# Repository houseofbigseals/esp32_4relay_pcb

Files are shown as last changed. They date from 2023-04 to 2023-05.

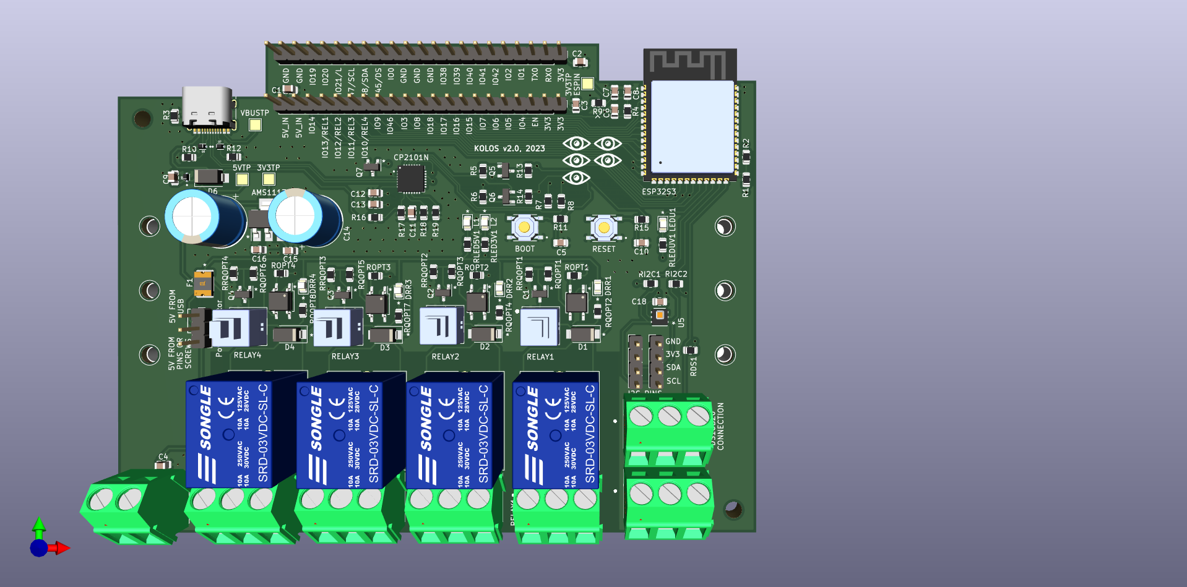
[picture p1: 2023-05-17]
esp32_4_relay3.png

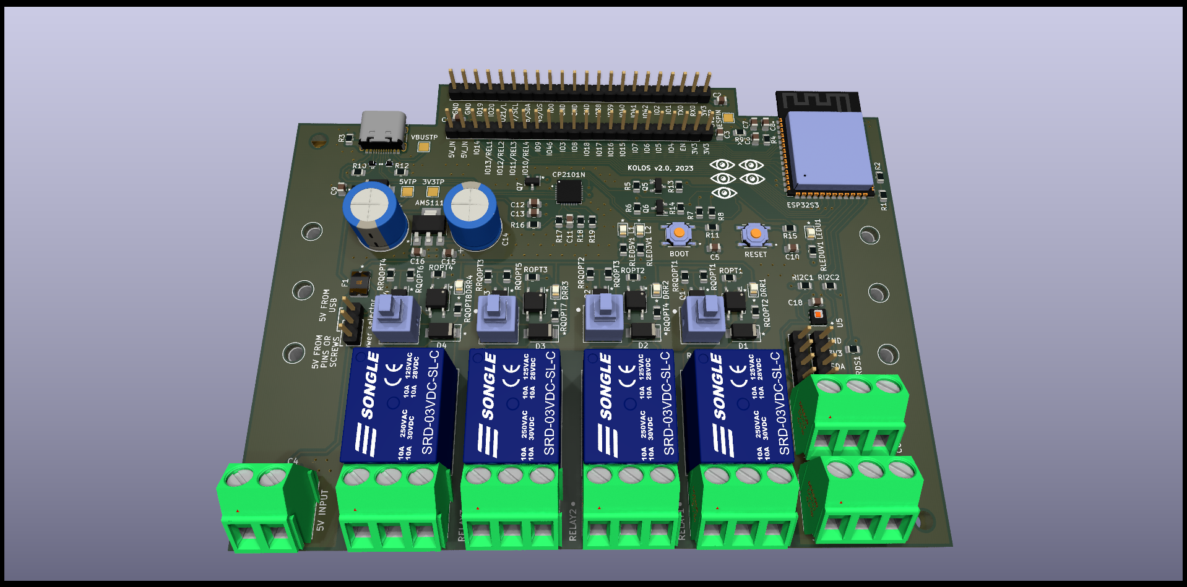
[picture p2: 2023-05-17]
esp32_4_relay.png

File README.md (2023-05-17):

KOLOS is an automation module based on ESP32-S3, designed for remote control of laboratory equipment - AC devices, sensors, indicators. Designed to manage environmental control systems for laboratory greenhouses with higher plants.  

Designed on a 4-layer printed circuit board, has dimensions of 124x95 mm.  
Powered by 5V via USB-C or screw connector, it has built-in surge protection with a self-resetting fuse. ESP32 is powered by a built-in AMS-1117-3.3 stabilizer.  
The board has expansion pins for connecting additional equipment to the controller, as well as screw connectors for connecting sensors using the 1-Wire protocol. The firmware of the controller and communication with the PC is done through the built-in USB-UART converter CP2102N. The board contains four relay channels controlled via an optocoupler and an HDC1080 temperature-humidity sensor.  
Mounting can be done in the housing with M3 screws or on a DIN rail, for which fasteners are provided.  
The firmware is implemented on the basis of the ESP-HOME framework for integrating the product into the Home Assistant environment. The system is configured so that the user can securely access the board remotely, via a Wireguard network, or locally.  

The pcb contains:  
- 4 5v relay module
- buttons for manual switching of the relay state in an emergency situation  
- optocoupler for relay control from the controller
- AMS-1117-3.3.
- USB-UART converter CP2102N.
- USB type-c for power and connection to a PC
- expansion pins for ESP32
- temperature-humidity sensor HDC1080
- expansion pins for connecting sensors via 1-Wire

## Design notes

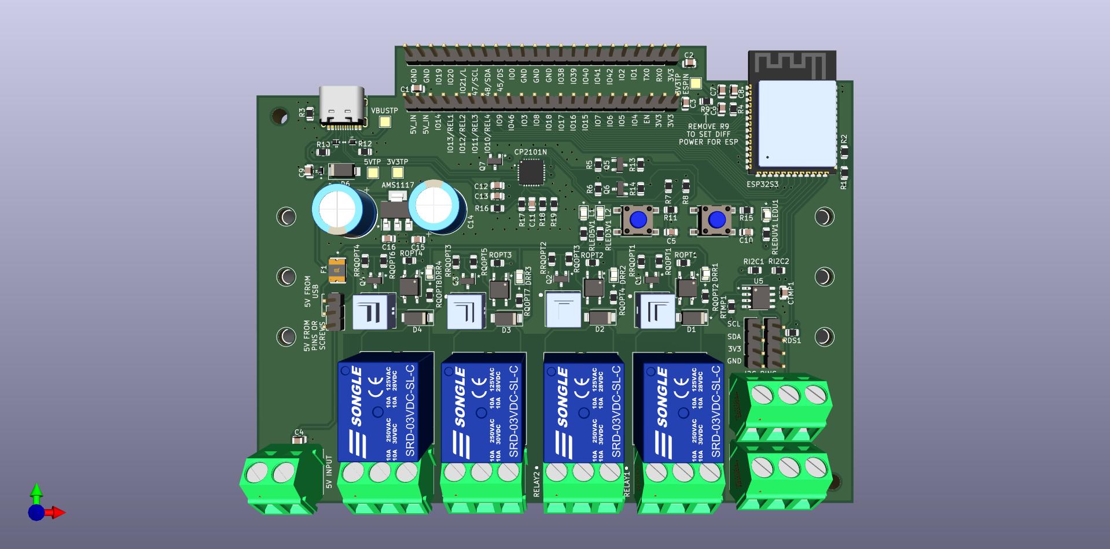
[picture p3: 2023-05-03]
esp32_4_relay.jpg

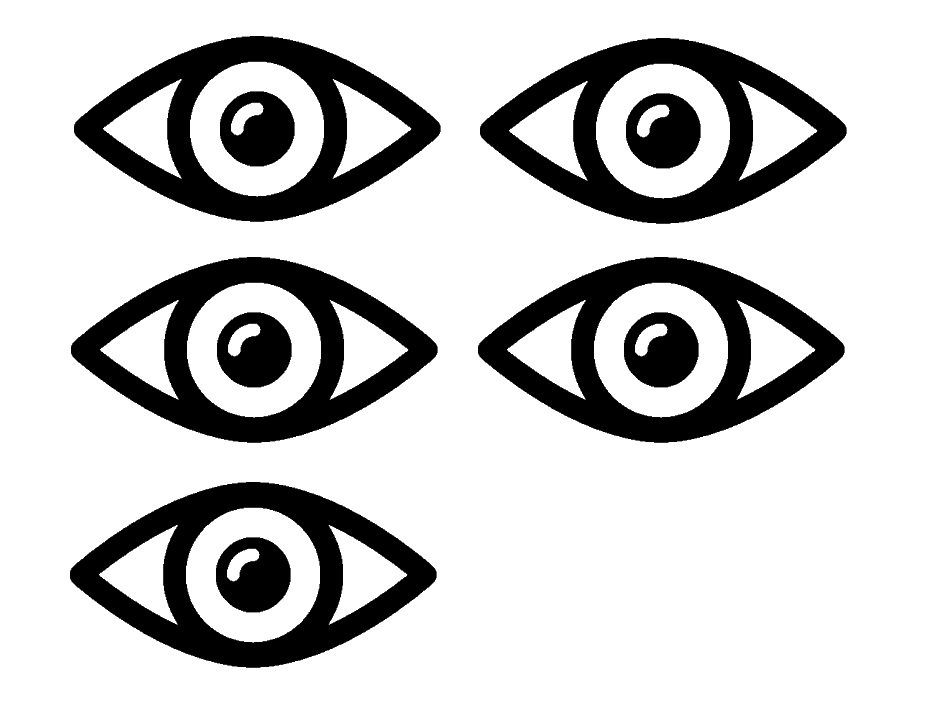
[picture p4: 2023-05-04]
five_eyed.png

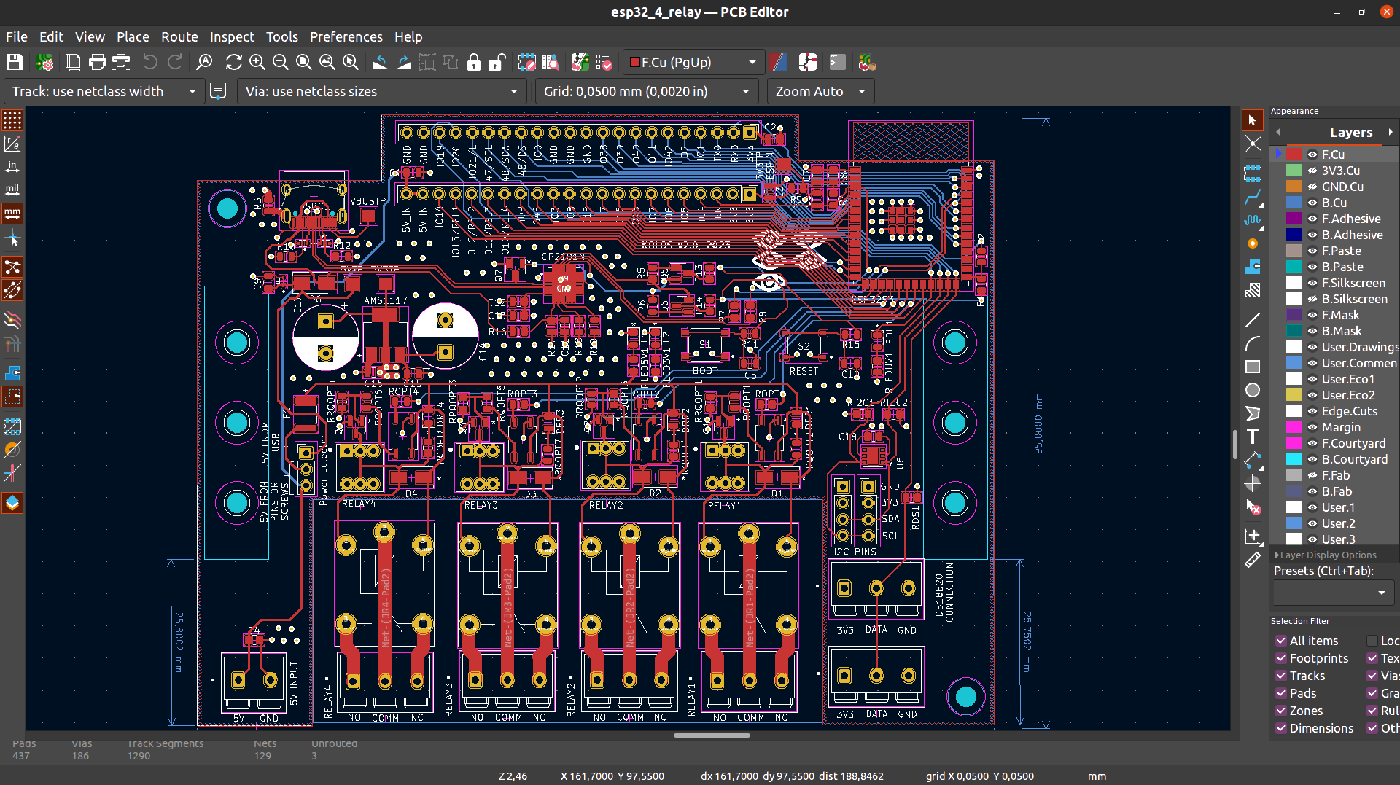
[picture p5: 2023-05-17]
esp32-4relay-sch.png

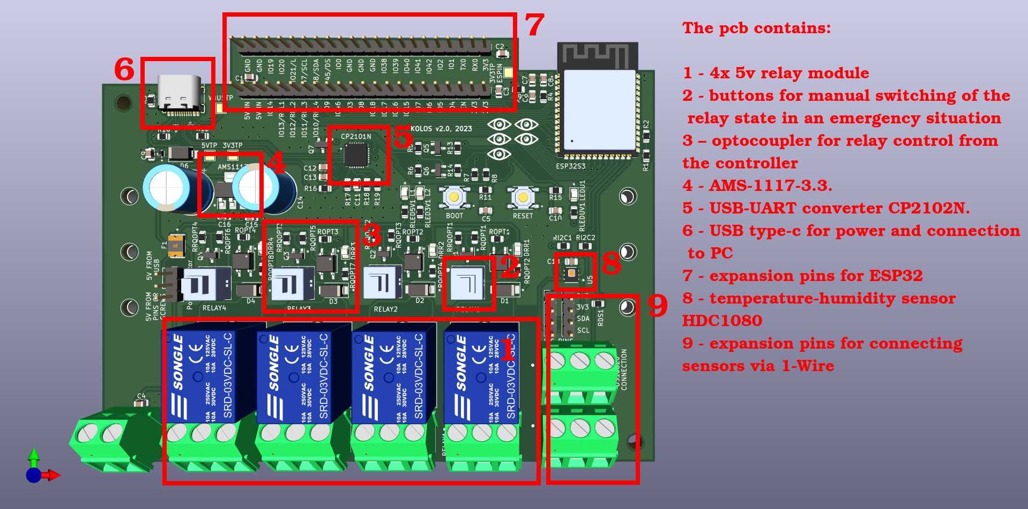
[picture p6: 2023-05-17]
esp32_4_relay3-noted.png

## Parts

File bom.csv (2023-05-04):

Designator | Footprint | Quantity | Value | LCSC Part #
AMS1 | SOT-223-3_TabPin2 | 1 | AMS1117-3.3 | C6186
C1, C12, C15, C16, C18, C2, C3, C4, C7 | 805 | 9 | 100nF | C49678
C11, C13, C9 | 805 | 3 | 10uF | C440198
C6 | 805 | 1 | 1uF | C28323
C8 | 805 | 1 | 22uF | C45783
CP1 | QFN50P500X500X80-29N | 1 | CP2102N-A02-GQFN28 | C964632
D1, D2, D3, D4 | D_SMA | 4 | 1N4007 | C95872
D5, D7, D8 | TVS_LESD5D5.0CT1G | 3 | LESD5D5.0CT1G | C383211
D6 | D_SMA | 1 | 1N5819 | C191023
DRR1, DRR2, DRR3, DRR4, L1, L2, LEDU1 | 805 | 7 | LED | C84256
DS1, DS2, JR1, JR2, JR3, JR4 | Screw-3-pin-conn | 6 | Screw_Terminal_01x03 | C784923
ESP32S3 | XCVR_ESP32-S3-WROOM-1-N8R2 | 1 | ESP32-S3-WROOM-1-N8R2 | C2913204
F1 | 1812 | 1 | Polyfuse | C84140
Q1, Q2, Q3, Q4, Q5, Q6 | SOT-23 | 6 | L8050QLT1G | C8512
Q7 | SOT-23 | 1 | 2N7002 | C8545
R1, R2 | 805 | 2 | 22R | C17561
R10, R12, RLED3V1, RLED5V1, RLEDUV1 | 805 | 5 | 5K1 | C27834
R11, R13, R14, R15, R7, R8, R9 | 805 | 7 | 0R | C17477
R16 | 805 | 1 | 22.1K | C17560
R17 | 805 | 1 | 47.5K | C17713
R18, RQOPT1, RQOPT3, RQOPT5, RQOPT6 | 805 | 5 | 1K | C17513
R3 | 805 | 1 | 1M | C17514
R4, R5, R6, RRQOPT1, RRQOPT2, RRQOPT3, RRQOPT4 | 805 | 7 | 10K | C17414
RDS1, RI2C1, RI2C2 | 805 | 3 | 4K7 | C17673
RELAY1, RELAY2, RELAY3, RELAY4 | Relay_T75 | 4 | SRD-05VDC-SL-C | C35449
ROPT1, ROPT2, ROPT3, ROPT4 | 805 | 4 | 330R | C17630
RQOPT2, RQOPT4, RQOPT7, RQOPT8 | 805 | 4 | 2K2 | C17520
S1, S2 | SW_TS-1187A-B-A-B | 2 | TS-1187A-B-A-B | C318884
SW1, SW2, SW3, SW4 | switch-dpdt | 4 | SW_Push_DPDT | C318862
TERM_POW1 | Screw-2-pin-conn | 1 | Screw_Terminal_01x02 | C784922
U1, U2, U3, U4 | SOP-4_3.8x4.1mm_P2.54mm | 4 | PC817 | C6649
U5 | Texas_PWSON-N6 | 1 | HDC1080 | C82227
USBC1 | USB_C_Receptacle_HRO_TYPE-C-31-M-12 | 1 | USB_C_Receptacle_USB2.0 | C165948

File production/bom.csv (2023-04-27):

Designator | Footprint | Quantity | Value | LCSC Part #
3V1, 5V1, ESP323V3, VBUS1 | TestPoint_Pad_2.0x2.0mm | 4 | TestPoint
AMS1 | SOT-223-3_TabPin2 | 1 | AMS1117-3.3
C1, C10, C2, C3, C4, C5, CTMP1 | 0805 | 7 | 100 nF
C11, C13, C9 | 0805 | 3 | 10uF
C12, C15, C16, C7 | 0805 | 4 | 100nF
C14 | CP_Radial_D10.0mm_P5.00mm | 1 | 10uF
C17 | CP_Radial_D10.0mm_P5.00mm | 1 | 10 uF
C6 | 0805 | 1 | 1uF
C8 | 0805 | 1 | 22uF
CONNL1, CONNR1 | PinHeader_1x22_P2.54mm_Vertical | 2 | Conn_01x22_Male
CONNPOW1 | PinHeader_1x03_P2.54mm_Vertical | 1 | Conn_01x03_Male
CP1 | QFN50P500X500X80-29N | 1 | CP2102N-A02-GQFN28
D1, D2, D3, D4 | D_SMA | 4 | 1N4007
D5, D7, D8 | TVS_LESD5D5.0CT1G | 3 | LESD5D5.0CT1G
D6 | D_SMA | 1 | 1N5819
DRA1, DRA2 | DINRailAdapter_3xM3_PhoenixContact_1201578 | 2 | DIN_Rail_Adapter
DRR1, DRR2, DRR3, DRR4, L1, L2, LEDU1 | 0805 | 7 | LED
DS1, DS2, JR1, JR2, JR3, JR4 | Screw-3-pin-conn | 6 | Screw_Terminal_01x03
ESP32S3 | XCVR_ESP32-S3-WROOM-1-N8R2 | 1 | ESP32-S3-WROOM-1-N8R2 | C2913204
F1 | 1812 | 1 | Polyfuse
H1, H2 | MountingHole_3.2mm_M3_DIN965 | 2 | MountingHole
I2C1, I2C2 | PinHeader_1x04_P2.54mm_Vertical | 2 | Conn_01x04_Male
Q1, Q2, Q3, Q4, Q5, Q6 | SOT-23 | 6 | L8050QLT1G
Q7 | SOT-23 | 1 | 2N7002
R1, R2 | 0805 | 2 | 22R
R10, R12 | 0805 | 2 | 5.1K
R11, R13, R14, R15, R7, R8, R9 | 0805 | 7 | 0R
R16 | 0805 | 1 | 22.1K
R17 | 0805 | 1 | 47.5K
R18, RQOPT1, RQOPT3, RQOPT5, RQOPT6 | 0805 | 5 | 1K
R19, R4, R5, R6 | 0805 | 4 | 10K
R3 | 0805 | 1 | 1M
RDS1, RI2C1, RI2C2, RTMP1 | 0805 | 4 | 4K7
RELAY1, RELAY2, RELAY3, RELAY4 | Relay_T75 | 4 | SRD-05VDC-SL-C
RLED3V1, RLED5V1, RLEDUV1 | 0805 | 3 | 5K1
ROPT1, ROPT2, ROPT3, ROPT4 | 0805 | 4 | 330R
RQOPT2, RQOPT4, RQOPT7, RQOPT8 | 0805 | 4 | 2K2
SW1, SW2, SW3, SW4 | switch-dpdt | 4 | SW_Push_DPDT
SW5, SW6 | SW_Push_1P1T_NO_6x6mm_H9.5mm | 2 | SW_DIP_x01
TERM_POW1 | Screw-2-pin-conn | 1 | Screw_Terminal_01x02
U1, U2, U3, U4 | SOP-4_3.8x4.1mm_P2.54mm | 4 | PC817
U5 | SOIC-8_3.9x4.9mm_P1.27mm | 1 | TMP75AIDR
USBC1 | USB_C_Receptacle_HRO_TYPE-C-31-M-12 | 1 | USB_C_Receptacle_USB2.0

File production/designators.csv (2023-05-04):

3V1:1
5V1:1
AMS1:1
C1:1
C10:1
C11:1
C12:1
C13:1
C14:1
C15:1
C16:1
C17:1
C18:1
C2:1
C3:1
C4:1
C5:1
C6:1
C7:1
C8:1
C9:1
CONNL1:1
CONNPOW1:1
CONNR1:1
CP1:1
D1:1
D2:1
D3:1
D4:1
D5:1
D6:1
D7:1
D8:1
DRA1:1
DRA2:1
DRR1:1
DRR2:1
DRR3:1
DRR4:1
DS1:1
DS2:1
ESP323V3:1
ESP32S3:1
F1:1
G***:1
H1:1
H2:1
I2C1:1
I2C2:1
JR1:1
JR2:1
JR3:1
JR4:1
L1:1
L2:1
LEDU1:1
Q1:1
Q2:1
Q3:1
Q4:1
Q5:1
Q6:1
Q7:1
R1:1
R10:1
R11:1
R12:1
R13:1
R14:1
R15:1
R16:1
R17:1
R18:1
R19:1
R2:1
R3:1
R4:1
R5:1
R6:1
R7:1
R8:1
R9:1
RDS1:1
RELAY1:1
RELAY2:1
RELAY3:1
RELAY4:1
RI2C1:1
RI2C2:1
RLED3V1:1
RLED5V1:1
RLEDUV1:1
ROPT1:1
ROPT2:1
ROPT3:1
ROPT4:1
RQOPT1:1
RQOPT2:1
RQOPT3:1
RQOPT4:1
RQOPT5:1
RQOPT6:1
RQOPT7:1
RQOPT8:1
RRQOPT1:1
RRQOPT2:1
RRQOPT3:1
RRQOPT4:1
S1:1
S2:1
SW1:1
SW2:1
SW3:1
SW4:1
TERM_POW1:1
U1:1
U2:1
U3:1
U4:1
U5:1
USBC1:1
VBUS1:1

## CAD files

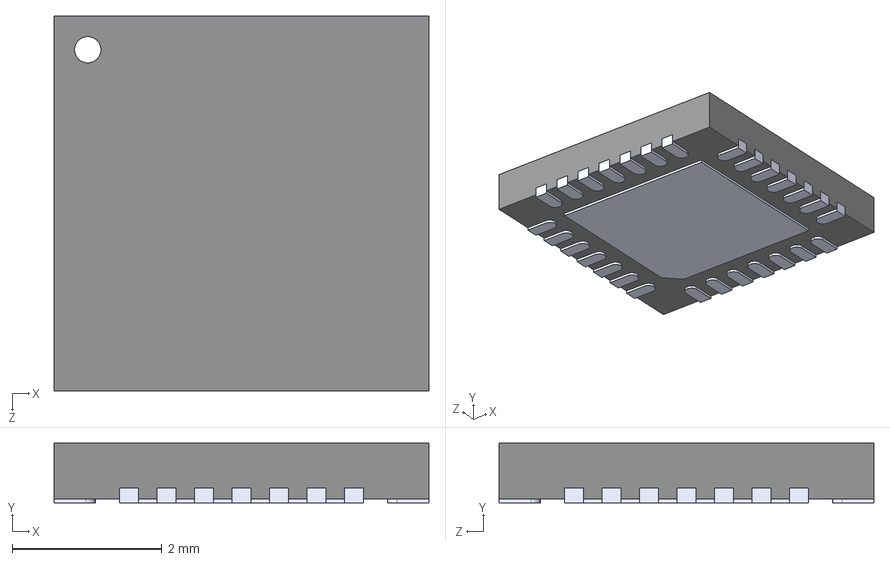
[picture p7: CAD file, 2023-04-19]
CP2102N-A02-GQFN28/CP2102N-A02-GQFN28.step
5.00 x 0.8 x 5.00 mm

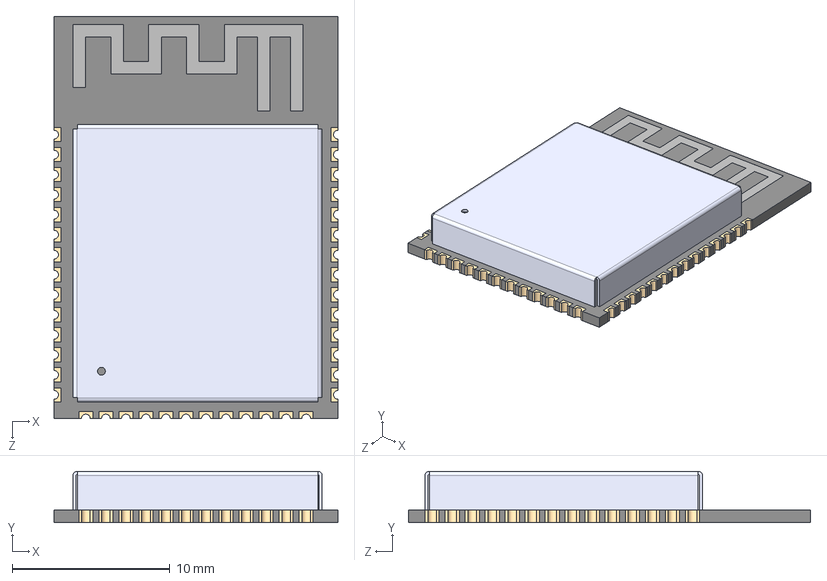
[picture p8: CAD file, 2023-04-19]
ESP32-S3-WROOM-1-N8R2/ESP32-S3-WROOM-1-N8R2.step
18.0 x 3.25 x 25.5 mm

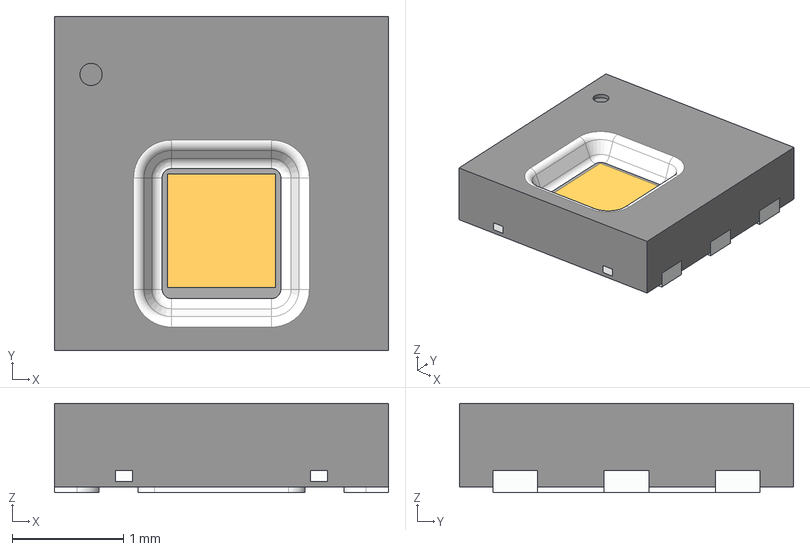
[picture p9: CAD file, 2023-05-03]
HDC1080.STEP
3.00 x 3.00 x 0.8 mm
BODY-SON_118_1
FRAME-DMB0006A_77_1_1
FRAME-DMB0006A_77_2_1
FRAME-DMB0006A_77_3_1
FRAME-DMB0006A_77_4_1
FRAME-DMB0006A_77_5_1
FRAME-DMB0006A_77_6_1
FRAME-DMB0006A_77_7_1
DIE_1_1

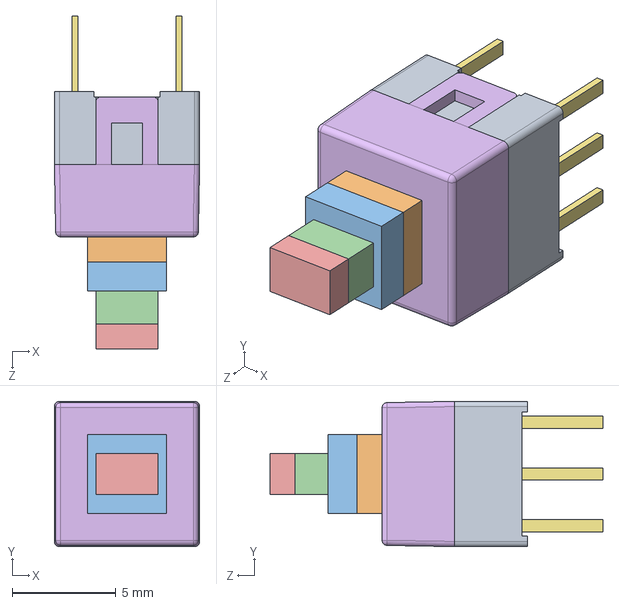
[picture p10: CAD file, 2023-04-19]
latching-dpdt-push-switch-7x7mm-1.snapshot.1/LatchSwitch_7x7.STEP
7.00 x 7.00 x 16.1 mm

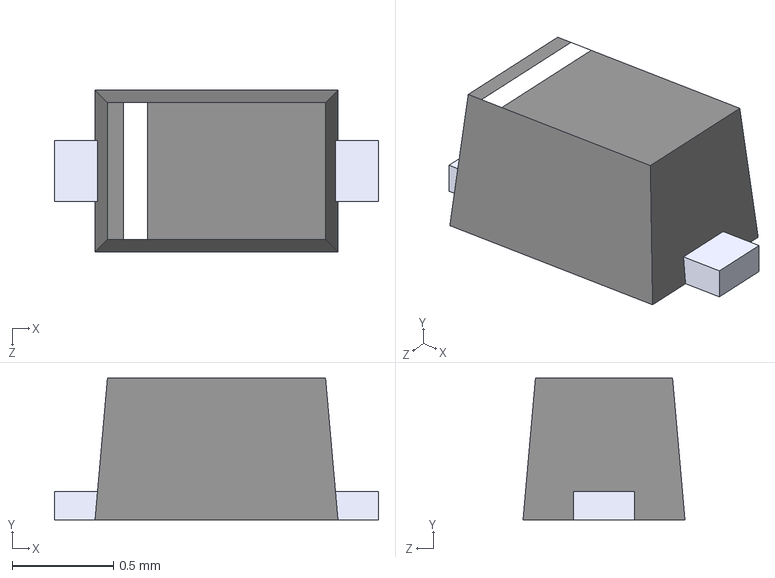
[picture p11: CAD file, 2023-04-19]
LESD5D5.0CT1G/LESD5D5.0CT1G.step
1.60 x 0.7 x 0.8 mm

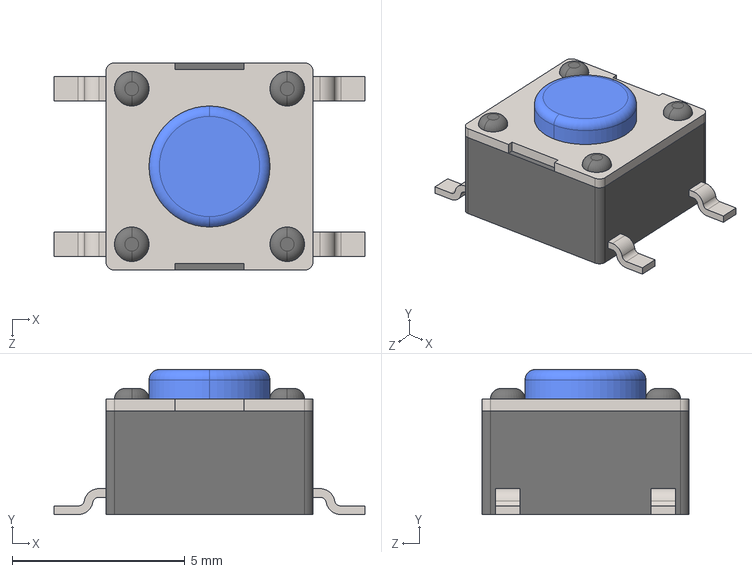
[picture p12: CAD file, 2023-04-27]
push-button-27.snapshot.4/PushButton.STEP
9.00 x 4.20 x 6.00 mm

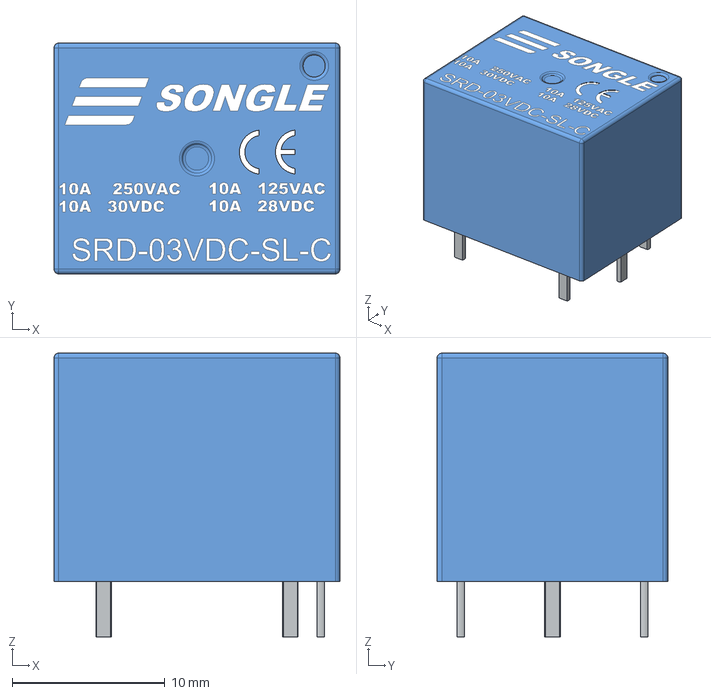
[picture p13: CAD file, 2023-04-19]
Relay-SRD-05VDC-SL-C/Relay - SRD-03VDC-SL-C.stp
18.7 x 15.1 x 18.6 mm

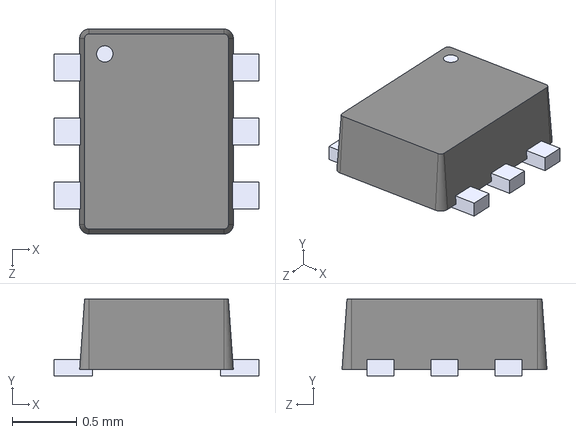
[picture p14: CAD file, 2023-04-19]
TMP102AIDRLR/TMP102AIDRLR.step
1.60 x 0.6 x 1.60 mm

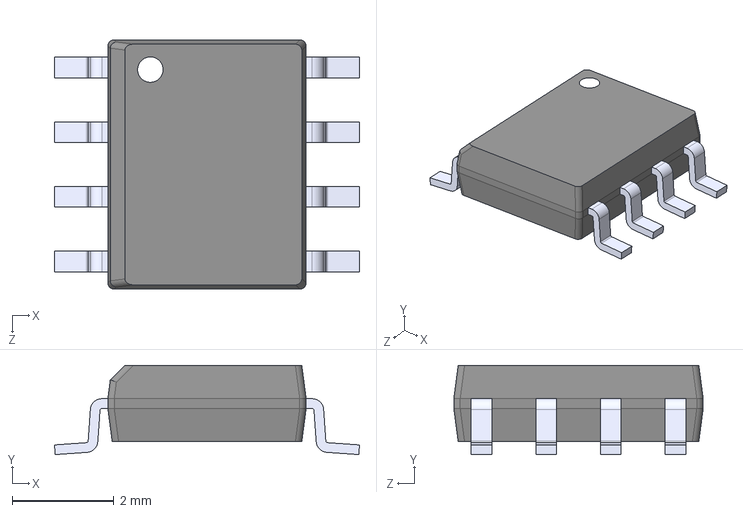
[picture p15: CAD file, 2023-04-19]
TMP75AIDR/TMP75AIDR.STEP
5.99 x 1.75 x 4.90 mm

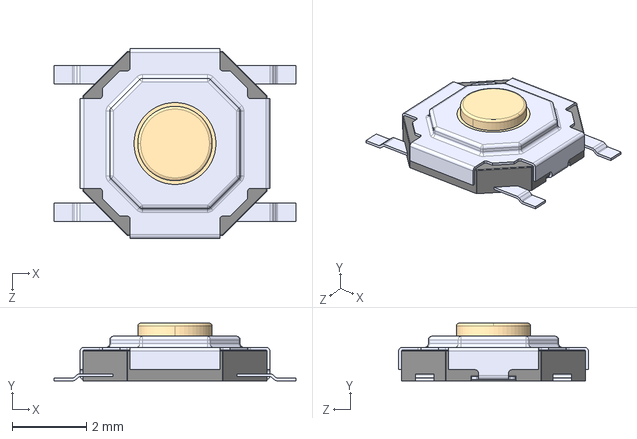
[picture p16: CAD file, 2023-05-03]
TS-1187A-B-A-B/TS-1187A-B-A-B.step
6.50 x 1.55 x 5.10 mm

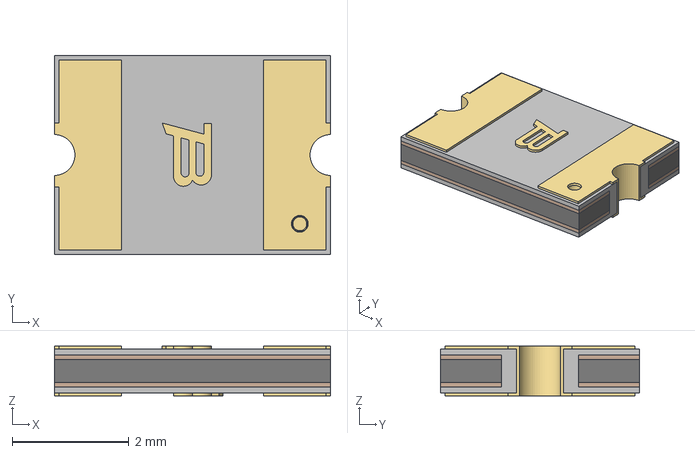
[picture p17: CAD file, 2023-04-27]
MF-MSMF-C0.85.stp
4.73 x 3.41 x 0.85 mm

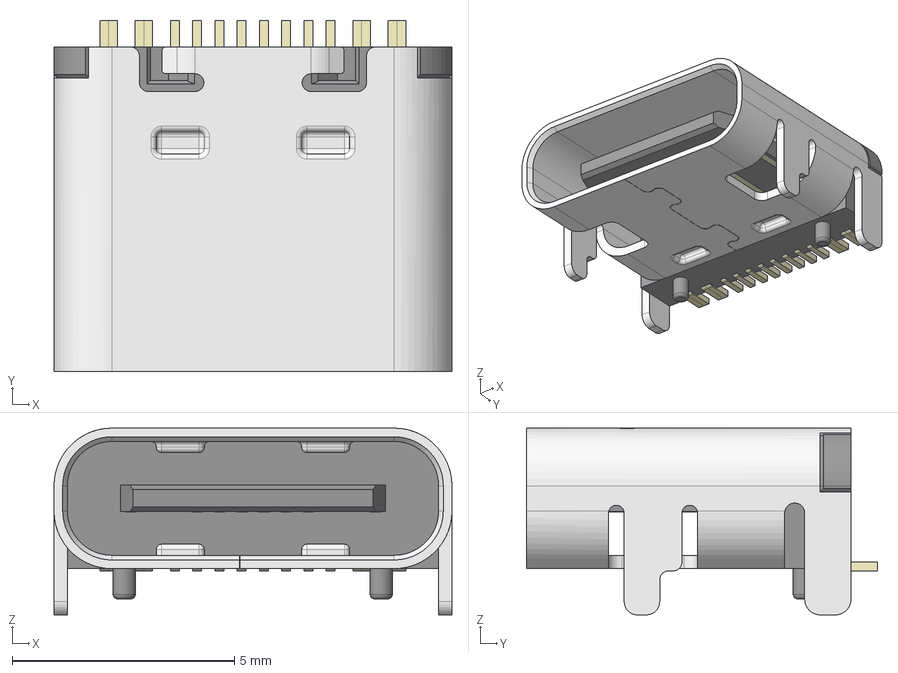
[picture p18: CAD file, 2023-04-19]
HRO_TYPE-C-31-M-12.step
8.95 x 7.90 x 4.20 mm

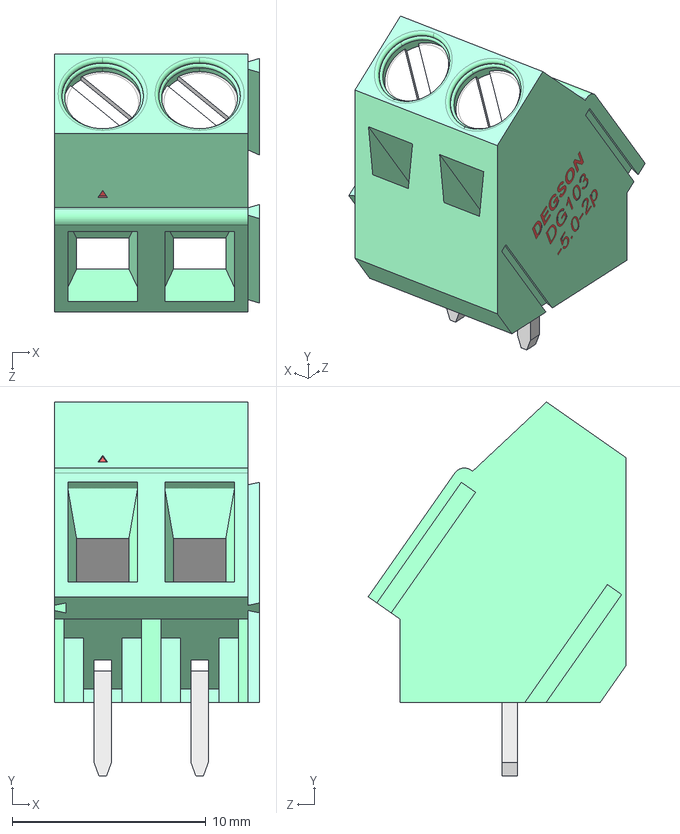
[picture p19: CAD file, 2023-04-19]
3-pin-screw-conn/DG103-5.0-02P-14-00AH.STEP
10.6 x 19.3 x 13.3 mm

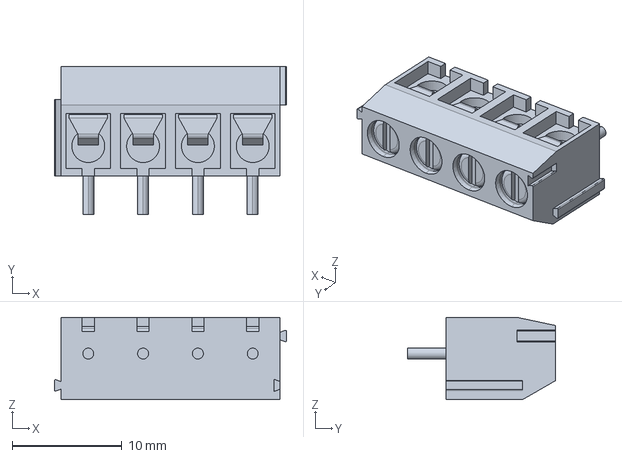
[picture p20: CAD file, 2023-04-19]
4_pin_screw_retminal/1776266-4.step
21.2 x 13.5 x 7.50 mm

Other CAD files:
3-pin-screw-conn/DG103-5.0-03P-14-00AH.STEP
latching-dpdt-push-switch-7x7mm-1.snapshot.1/LatchSwitch_7x7.IGS
push-button-27.snapshot.4/PushButton.SLDPRT
push-button-27.snapshot.4/PushButton.STL

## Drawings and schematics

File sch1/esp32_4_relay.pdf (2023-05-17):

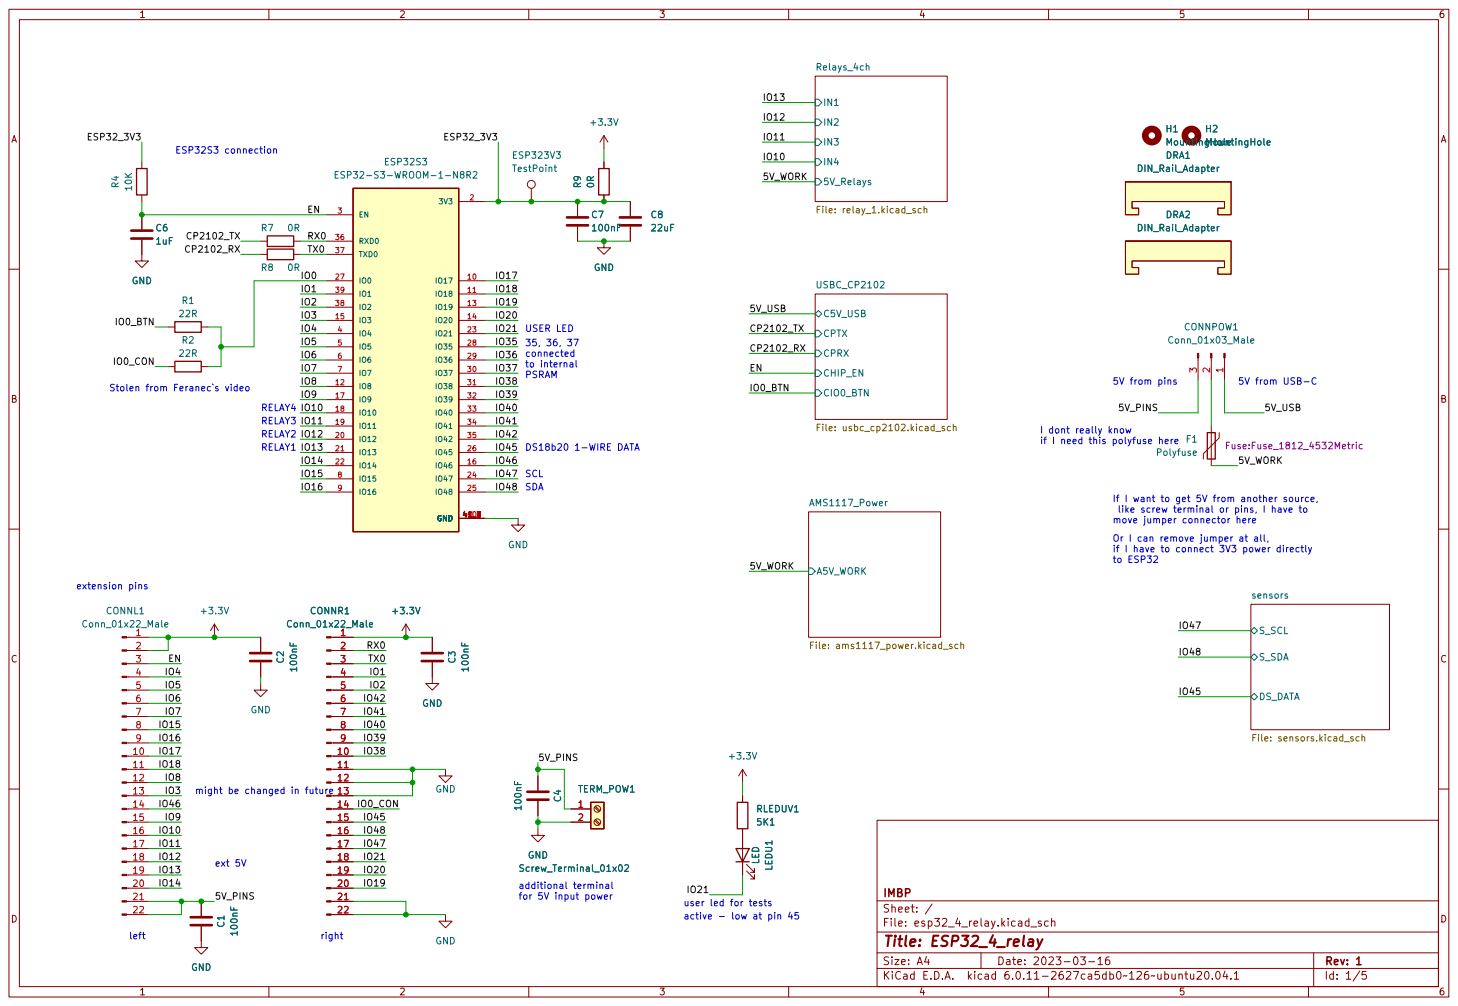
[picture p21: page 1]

Stolen from Feranec`s video

if I need this polyfuse here RELAY4 might be changed in future RELAY1 RELAY2

If I want to get 5V from another source,

if I have to connect 3V3 power directly

user led for tests
active - low at pin 45

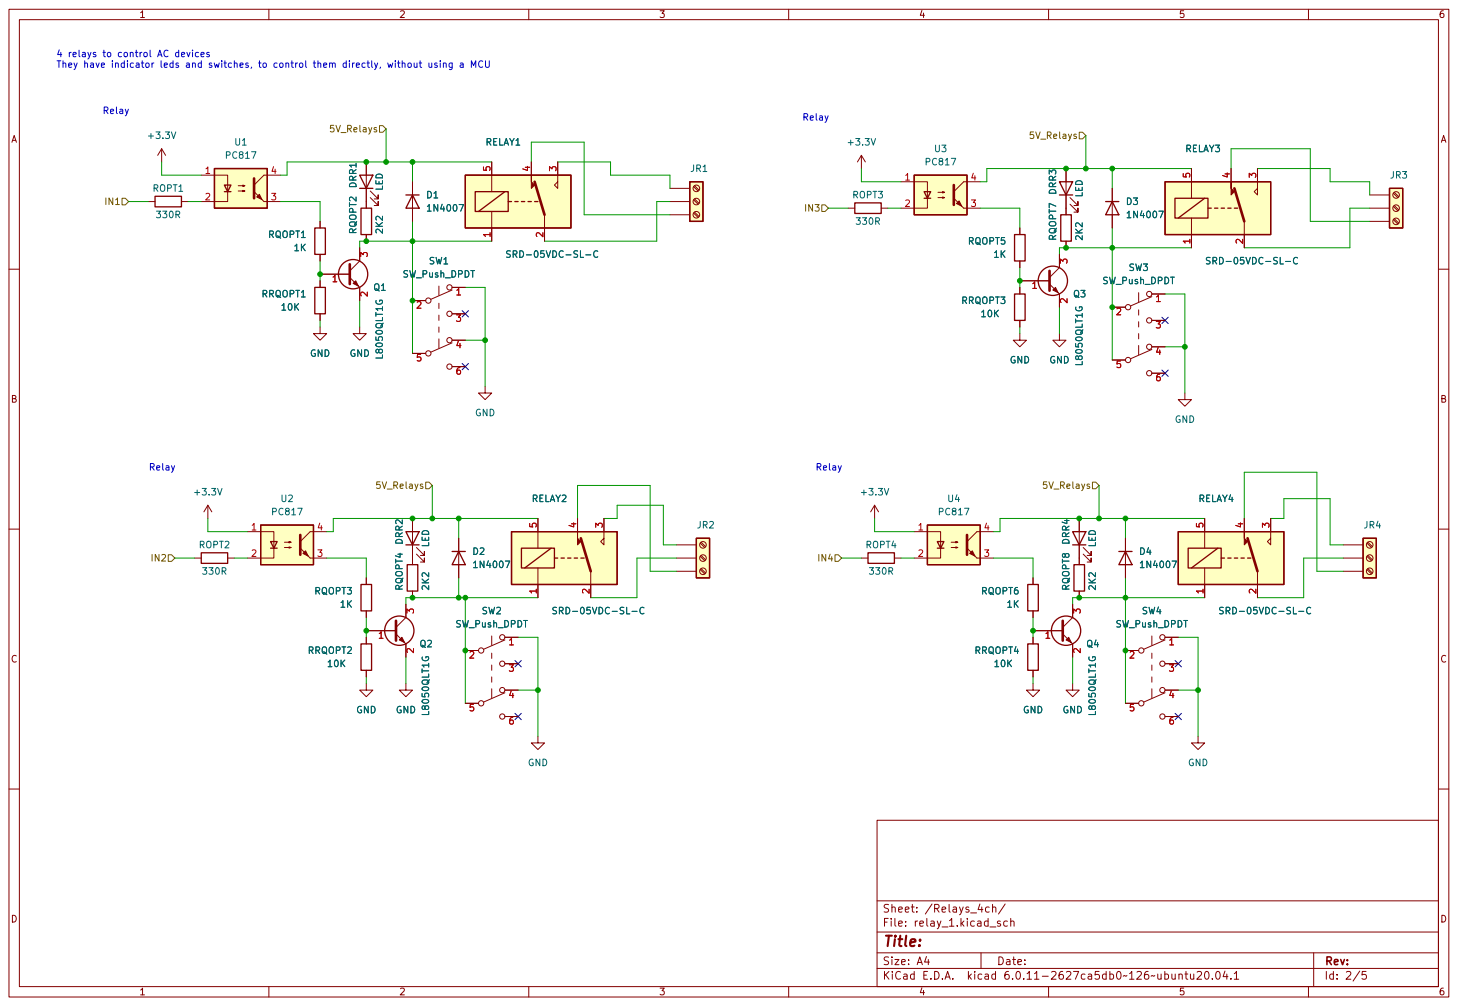
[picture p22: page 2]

Id: 2/5 Title: File: relay_1.kicad_sch Sheet: /Relays_4ch/ 1

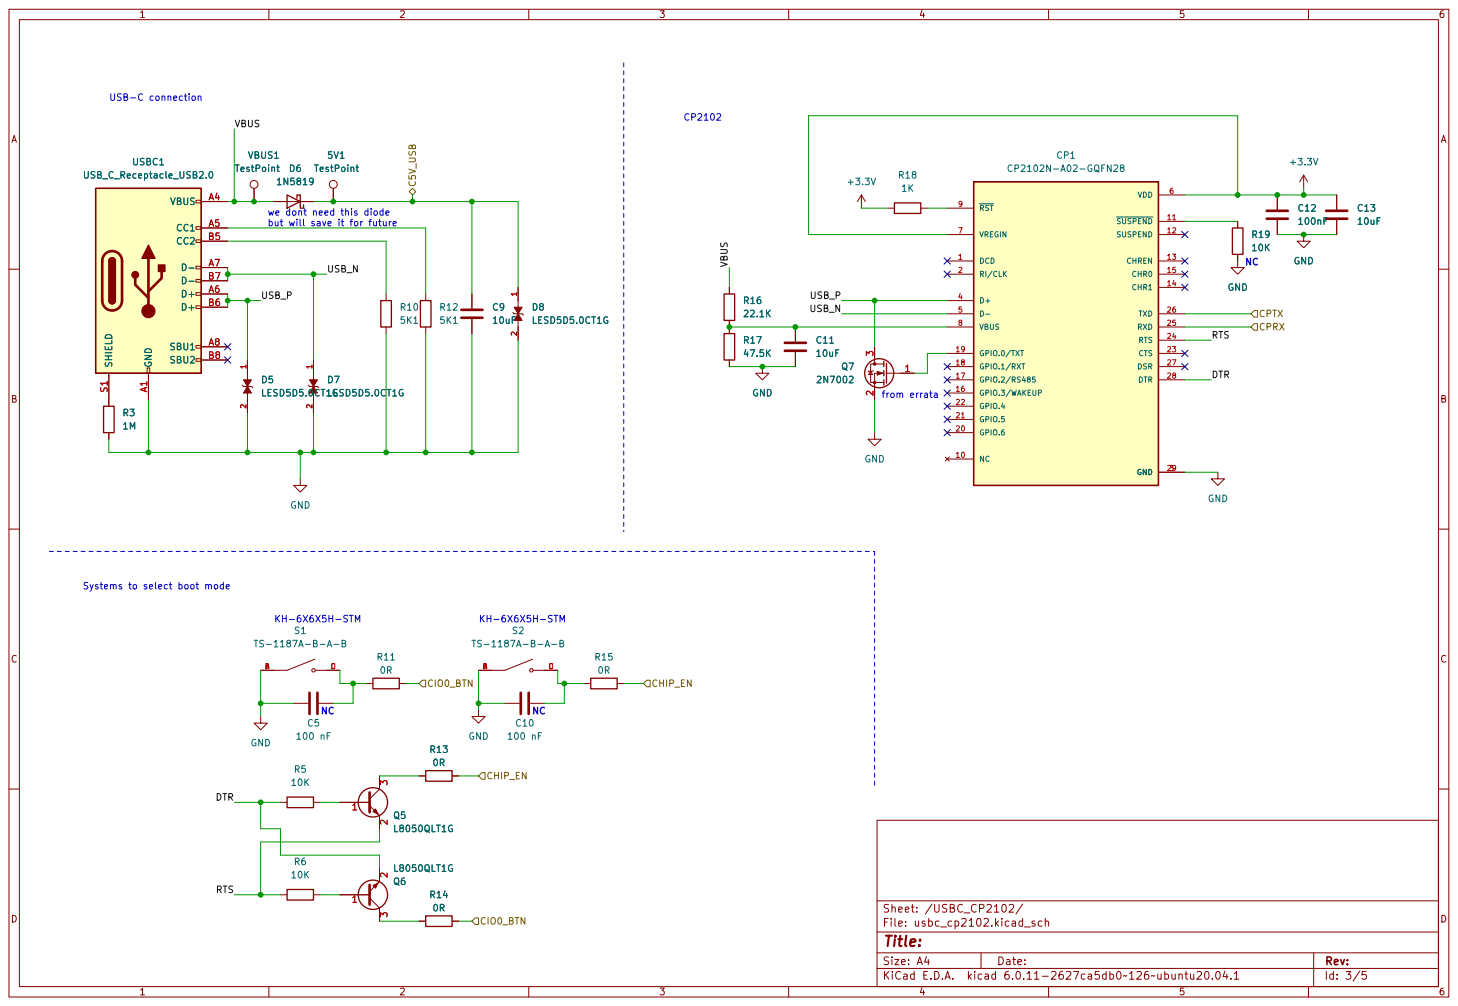
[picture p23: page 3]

USB_P we dont need this diode

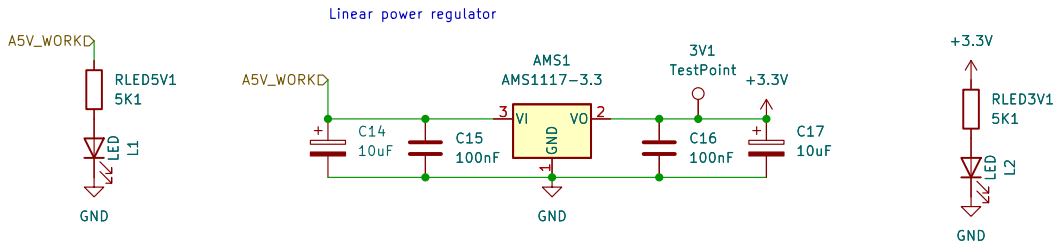
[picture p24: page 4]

Id: 4/5 Title: File: ams1117_power.kicad_sch Sheet: /AMS1117_Power/ GND

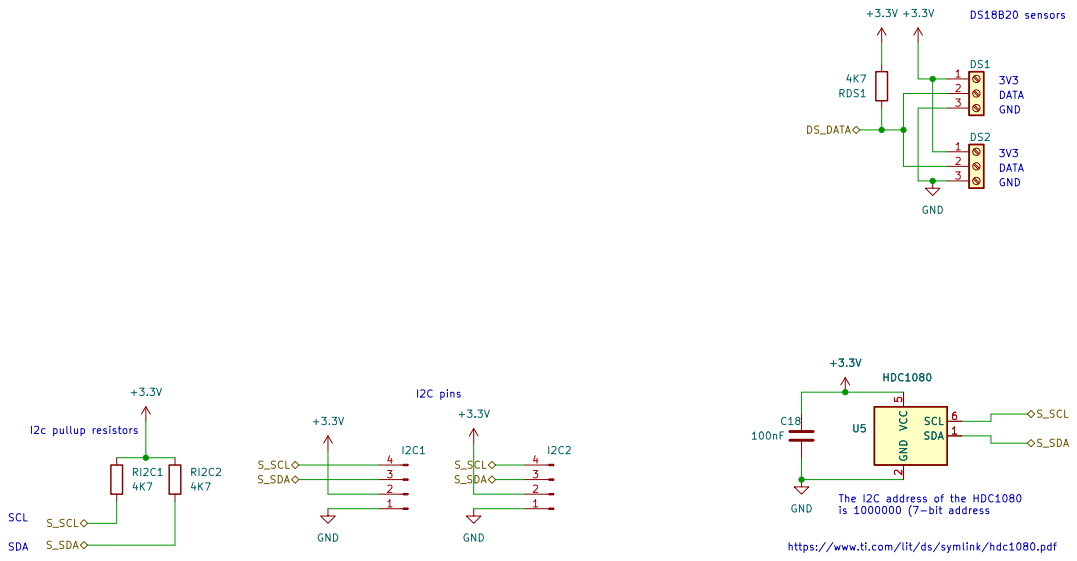
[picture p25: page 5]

https://www.ti.com/lit/ds/symlink/hdc1080.pdf The I2C address of the HDC1080

Id: 5/5 Title: File: sensors.kicad_sch Sheet: /sensors/

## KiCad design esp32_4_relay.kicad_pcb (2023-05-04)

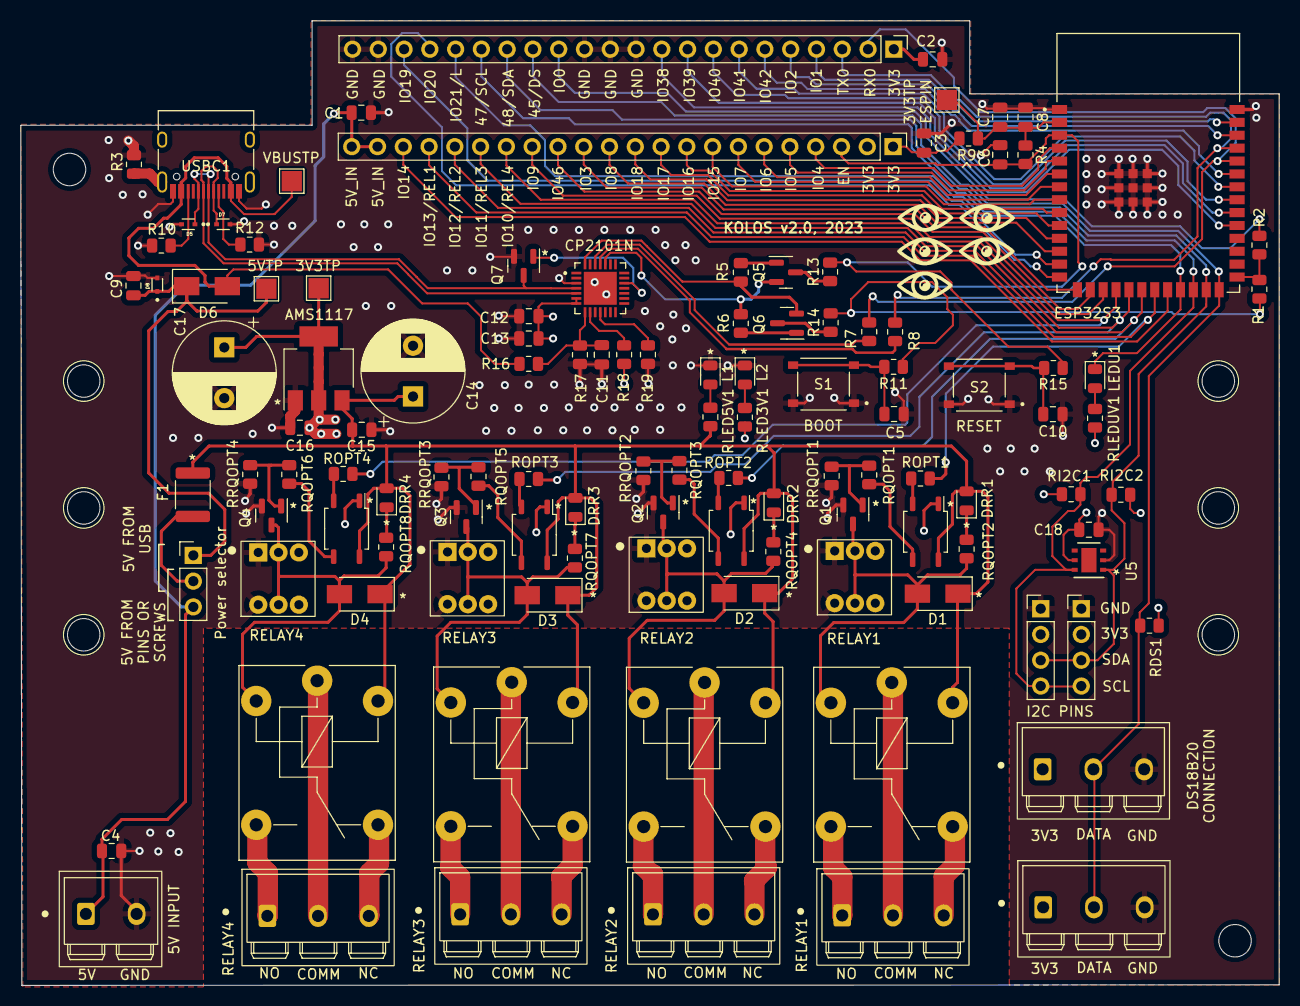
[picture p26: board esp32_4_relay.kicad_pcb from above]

Board: 4 copper layers, 124.0 x 95.0 mm, 121 parts (0 on the bottom side), 98 nets.

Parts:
3V1, 5V1: TestPoint; TestPoint_Pad_2.0x2.0mm
AMS1: AMS1117-3.3; SOT-223-3_TabPin2
C1, C2, C3, C4, C7, C12, C15, C16, C18: 100nF; C_0805_2012Metric
C5, C10: 100 nF; C_0805_2012Metric
C6: 1uF; C_0805_2012Metric
C8: 22uF; C_0805_2012Metric
C9, C11, C13: 10uF; C_0805_2012Metric
C14, C17: 10uF; CP_Radial_D10.0mm_P5.00mm
CONNL1: Conn_01x22_Male; PinHeader_1x22_P2.54mm_Vertical
CONNPOW1: Conn_01x03_Male; PinHeader_1x03_P2.54mm_Vertical
CONNR1: Conn_01x22_Male; PinHeader_1x22_P2.54mm_Vertical
CP1: CP2102N-A02-GQFN28; QFN50P500X500X80-29N
D1, D2, D3, D4: 1N4007; D_SMA
D5, D7, D8: LESD5D5.0CT1G; TVS_LESD5D5.0CT1G
D6: 1N5819; D_SMA
DRA1, DRA2: DIN_Rail_Adapter; DINRailAdapter_3xM3_PhoenixContact_1201578
DRR1, DRR2, DRR3, DRR4: LED; LED_0805_2012Metric
DS1, DS2: Screw_Terminal_01x03; Screw-3-pin-conn
ESP32S3: ESP32-S3-WROOM-1-N8R2; XCVR_ESP32-S3-WROOM-1-N8R2
ESP323V3: TestPoint; TestPoint_Pad_2.0x2.0mm
F1: Polyfuse; Fuse_1812_4532Metric
H1, H2: MountingHole; MountingHole_3.2mm_M3_DIN965
I2C1, I2C2: Conn_01x04_Male; PinHeader_1x04_P2.54mm_Vertical
JR1, JR2, JR3, JR4: Screw_Terminal_01x03; Screw-3-pin-conn
L1, L2: LED; LED_0805_2012Metric
LEDU1: LED; LED_0805_2012Metric
Q1, Q2, Q3, Q4, Q5, Q6: L8050QLT1G; SOT-23
Q7: 2N7002; SOT-23
R1, R2: 22R; R_0805_2012Metric
R3: 1M; R_0805_2012Metric
R4, R5, R6, R19: 10K; R_0805_2012Metric
R7, R8, R9, R11, R13, R14, R15: 0R; R_0805_2012Metric
R10, R12: 5K1; R_0805_2012Metric
R16: 22.1K; R_0805_2012Metric
R17: 47.5K; R_0805_2012Metric
R18: 1K; R_0805_2012Metric
RDS1: 4K7; R_0805_2012Metric
RELAY1, RELAY2, RELAY3, RELAY4: SRD-05VDC-SL-C; Relay_T75
RI2C1, RI2C2: 4K7; R_0805_2012Metric
RLED3V1, RLED5V1: 5K1; R_0805_2012Metric
RLEDUV1: 5K1; R_0805_2012Metric
ROPT1, ROPT2, ROPT3, ROPT4: 330R; R_0805_2012Metric
RQOPT1, RQOPT3, RQOPT5, RQOPT6: 1K; R_0805_2012Metric
RQOPT2, RQOPT4, RQOPT7, RQOPT8: 2K2; R_0805_2012Metric
RRQOPT1, RRQOPT2, RRQOPT3, RRQOPT4: 10K; R_0805_2012Metric
S1, S2: TS-1187A-B-A-B; SW_TS-1187A-B-A-B
SW1, SW2, SW3, SW4: SW_Push_DPDT; switch-dpdt
TERM_POW1: Screw_Terminal_01x02; Screw-2-pin-conn
U1, U2, U3, U4: PC817; SOP-4_3.8x4.1mm_P2.54mm
U5: HDC1080; Texas_PWSON-N6
USBC1: USB_C_Receptacle_USB2.0; USB_C_Receptacle_HRO_TYPE-C-31-M-12
VBUS1: TestPoint; TestPoint_Pad_2.0x2.0mm

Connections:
+3.3V: 3V1.1, AMS1.2 (VO), C2.2, C3.2, C12.1, C13.1, C16.1, C17.1, C18.1, CONNL1.1, CONNL1.2, CONNR1.1, CP1.6 (VDD), CP1.7 (VREGIN), DS1.1, DS2.1, I2C1.2, I2C2.2, R9.2, R18.1, RDS1.1, RI2C1.2, RI2C2.2, RLED3V1.2, RLEDUV1.2, U1.1, U2.1, U3.1, U4.1, U5.5 (VCC)
/5V_PINS: C1.2, C4.2, CONNL1.21, CONNL1.22, CONNPOW1.3, TERM_POW1.1
/5V_USB: 5V1.1, C9.1, CONNPOW1.1, D6.1 (K), D8.1
/5V_WORK: AMS1.3 (VI), C14.1, C15.1, D1.1 (K), D2.1 (K), D3.1 (K), D4.1 (K), DRR1.2 (A), DRR2.2 (A), DRR3.2 (A), DRR4.2 (A), F1.1, RELAY1.5, RELAY2.5, RELAY3.5, RELAY4.5, RLED5V1.2, U1.4, U2.4, U3.4, U4.4
/CP2102_RX: CP1.25 (RXD), R8.1
/CP2102_TX: CP1.26 (TXD), R7.1
/EN: C6.1, CONNL1.3, ESP32S3.3 (EN), R4.1, R13.2, R15.2
/ESP32_3V3: C7.1, C8.1, ESP32S3.2 (3V3), ESP323V3.1, R4.2, R9.1
/IO0: ESP32S3.27 (IO0), R1.2, R2.2
/IO0_BTN: R1.1, R11.2, R14.2
/IO0_CON: CONNR1.14, R2.1
/IO1: CONNR1.4, ESP32S3.39 (IO1)
/IO2: CONNR1.5, ESP32S3.38 (IO2)
/IO3: CONNL1.13, ESP32S3.15 (IO3)
/IO4: CONNL1.4, ESP32S3.4 (IO4)
/IO5: CONNL1.5, ESP32S3.5 (IO5)
/IO6: CONNL1.6, ESP32S3.6 (IO6)
/IO7: CONNL1.7, ESP32S3.7 (IO7)
/IO8: CONNL1.12, ESP32S3.12 (IO8)
/IO9: CONNL1.15, ESP32S3.17 (IO9)
/IO10: CONNL1.16, ESP32S3.18 (IO10), ROPT4.1
/IO11: CONNL1.17, ESP32S3.19 (IO11), ROPT3.1
/IO12: CONNL1.18, ESP32S3.20 (IO12), ROPT2.1
/IO13: CONNL1.19, ESP32S3.21 (IO13), ROPT1.1
/IO14: CONNL1.20, ESP32S3.22 (IO14)
/IO15: CONNL1.8, ESP32S3.8 (IO15)
/IO16: CONNL1.9, ESP32S3.9 (IO16)
/IO17: CONNL1.10, ESP32S3.10 (IO17)
/IO18: CONNL1.11, ESP32S3.11 (IO18)
/IO19: CONNR1.20, ESP32S3.13 (IO19)
/IO20: CONNR1.19, ESP32S3.14 (IO20)
/IO21: CONNR1.18, ESP32S3.23 (IO21), LEDU1.1 (K)
/IO38: CONNR1.10, ESP32S3.31 (IO38)
/IO39: CONNR1.9, ESP32S3.32 (IO39)
/IO40: CONNR1.8, ESP32S3.33 (IO40)
/IO41: CONNR1.7, ESP32S3.34 (IO41)
/IO42: CONNR1.6, ESP32S3.35 (IO42)
/IO45: CONNR1.15, DS1.2, DS2.2, ESP32S3.26 (IO45), RDS1.2
/IO46: CONNL1.14, ESP32S3.16 (IO46)
/IO47: CONNR1.17, ESP32S3.24 (IO47), I2C1.4, I2C2.4, RI2C1.1, U5.6 (SCL)
/IO48: CONNR1.16, ESP32S3.25 (IO48), I2C1.3, I2C2.3, RI2C2.1, U5.1 (SDA)
/RX0: CONNR1.2, ESP32S3.36 (RXD0), R7.2
/TX0: CONNR1.3, ESP32S3.37 (TXD0), R8.2
/USBC_CP2102/DTR: CP1.28 (DTR), Q6.2 (E), R5.2
/USBC_CP2102/RTS: CP1.24 (RTS), Q5.2 (E), R6.2
/USBC_CP2102/USB_N: CP1.5 (D-), D7.1, USBC1.A7 (D-), USBC1.B7 (D-)
/USBC_CP2102/USB_P: CP1.4 (D+), D5.1, Q7.3 (D), USBC1.A6 (D+), USBC1.B6 (D+)
/USBC_CP2102/VBUS: D6.2 (A), R16.2, USBC1.A4 (VBUS), USBC1.A9 (VBUS), USBC1.B4 (VBUS), USBC1.B9 (VBUS), VBUS1.1
GND: AMS1.1 (GND), C1.1, C2.1, C3.1, C4.1, C5.1, C6.2, C7.2, C8.2, C9.2, C10.1, C11.2, C12.2, C13.2, C14.2, C15.2, C16.2, C17.2, C18.2, CONNR1.11, CONNR1.12, CONNR1.13, CONNR1.21, CONNR1.22, CP1.3 (GND), CP1.29 (GND), D5.2, D7.2, D8.2, DS1.3, DS2.3, ESP32S3.1 (GND), ESP32S3.40 (GND), ESP32S3.41_1 (GND), ESP32S3.41_2 (GND), ESP32S3.41_3 (GND), ESP32S3.41_4 (GND), ESP32S3.41_5 (GND), ESP32S3.41_6 (GND), ESP32S3.41_7 (GND), ESP32S3.41_8 (GND), ESP32S3.41_9 (GND), I2C1.1, I2C2.1, L1.1 (K), L2.1 (K), Q1.2 (E), Q2.2 (E), Q3.2 (E), Q4.2 (E), Q7.2 (S), R3.2, R10.2, R12.2, R17.1, R19.2, RRQOPT1.2, RRQOPT2.2, RRQOPT3.2, RRQOPT4.2, S1.A, S1.B, S2.A, S2.B, SW1.1 (A), SW1.4 (A), SW2.1 (A), SW2.4 (A), SW3.1 (A), SW3.4 (A), SW4.1 (A), SW4.4 (A), TERM_POW1.2, U5.2 (GND), USBC1.A1 (GND), USBC1.A12 (GND), USBC1.B1 (GND), USBC1.B12 (GND)
unnamed: C5.2, R11.1, S1.C, S1.D
unnamed: C10.2, R15.1, S2.C, S2.D
unnamed: C11.1, CP1.8 (VBUS), R16.1, R17.2
unnamed: CONNPOW1.2, F1.2
unnamed: CP1.9 (~RST), R18.2
unnamed: CP1.11 (~SUSPEND), R19.1
unnamed: CP1.19 (GPIO.0/TXT), Q7.1 (G)
unnamed: D1.2 (A), Q1.3 (C), RELAY1.1, RQOPT2.1, SW1.2 (B), SW1.5 (B)
unnamed: D2.2 (A), Q2.3 (C), RELAY2.1, RQOPT4.1, SW2.2 (B), SW2.5 (B)
unnamed: D3.2 (A), Q3.3 (C), RELAY3.1, RQOPT7.1, SW3.2 (B), SW3.5 (B)
unnamed: D4.2 (A), Q4.3 (C), RELAY4.1, RQOPT8.1, SW4.2 (B), SW4.5 (B)
unnamed: DRR1.1 (K), RQOPT2.2
unnamed: DRR2.1 (K), RQOPT4.2
unnamed: DRR3.1 (K), RQOPT7.2
unnamed: DRR4.1 (K), RQOPT8.2
unnamed: JR1.1, RELAY1.3
unnamed: JR1.2, RELAY1.2
unnamed: JR1.3, RELAY1.4
unnamed: JR2.1, RELAY2.3
unnamed: JR2.2, RELAY2.2
unnamed: JR2.3, RELAY2.4
unnamed: JR3.1, RELAY3.3
unnamed: JR3.2, RELAY3.2
unnamed: JR3.3, RELAY3.4
unnamed: JR4.1, RELAY4.3
unnamed: JR4.2, RELAY4.2
unnamed: JR4.3, RELAY4.4
unnamed: L1.2 (A), RLED5V1.1
unnamed: L2.2 (A), RLED3V1.1
unnamed: LEDU1.2 (A), RLEDUV1.1
unnamed: Q1.1 (B), RQOPT1.1, RRQOPT1.1
unnamed: Q2.1 (B), RQOPT3.1, RRQOPT2.1
unnamed: Q3.1 (B), RQOPT5.1, RRQOPT3.1
unnamed: Q4.1 (B), RQOPT6.1, RRQOPT4.1
unnamed: Q5.1 (B), R5.1
unnamed: Q5.3 (C), R13.1
unnamed: Q6.1 (B), R6.1
unnamed: Q6.3 (C), R14.1
unnamed: R3.1, USBC1.S1 (SHIELD)
unnamed: R10.1, USBC1.B5 (CC2)
unnamed: R12.1, USBC1.A5 (CC1)
unnamed: ROPT1.2, U1.2
unnamed: ROPT2.2, U2.2
unnamed: ROPT3.2, U3.2
unnamed: ROPT4.2, U4.2
unnamed: RQOPT1.2, U1.3
unnamed: RQOPT3.2, U2.3
unnamed: RQOPT5.2, U3.3
unnamed: RQOPT6.2, U4.3

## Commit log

2023-05-03 new pre-fabrication
    [4_relay_bom.csv, HDC1080.STEP, TS-1187A-B-A-B.step, ams1117_power.kicad_sch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]
2023-06-03 fix cp2102 transistor
    [usbc_cp2102.kicad_sch]
